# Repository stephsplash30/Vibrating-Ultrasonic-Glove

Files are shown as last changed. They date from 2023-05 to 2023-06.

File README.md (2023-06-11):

# Vibrating Ultrasonic Glove
Eric Zhu, Kate Saxen, and Katya Osipova

## Table of Contents
1. [Introduction](#Introduction)
2. [Initial Circuit](#Initial-Circuit)
3. [Final Design](#Final-Design)
4. [Testing Apparatus](#Testing-Apparatus)
5. [Sensor Mounting](#Sensor-Mounting)
6. [Adding Sensors](#Adding-Sensors)
7. [Initial Tests](#Initial-Tests)
8. [Mount Tests](#Mount-Tests)
9. [Hoodie Tests](#Hoodie-Tests)
10. [Conclusion](#Conclusion)

## Introduction 
For our project, we aim to create a vibrotactile tool that will provide feedback based on the distance to the nearest obstacle, serving as an ancillary device for people with low or no vision in addition to a white cane. The device could be used at home or in busier areas, such as a grocery store. We hope to expand usage to bustling streets. In such environments, white canes could take up too much space or may simply be unnecessary due to familiarity of the environment. Overall, the size of a white cane is the main disadvantage, as it can be a safety hazard to the user or the surrounding people. Additionally, the stigmatization of mobility aids such as the white cane makes those with disabilities less inclined to adopt it. By using this device as a replacement, or a supplement, precise distance information is gained, which is critical in mobility. Our goal is to be able to work as well as a white cane, while making our device more compact and seamless to use in comparison.



We will demonstrate the use of this device with ultrasonic sensing technology, which uses sound waves to measure distance; these waves are emitted at a frequency range too high for humans to hear. Ultrasonic waves do not interfere with radio and electromagnetic waves, used in other day-to-day devices, allowing for comfortable use in daily life.

Our device lies in a wide field of sensing technologies that have a plethora of applications in motion detection, distance measurement, and level gauge. For example, sonar technology is used in water with its high-frequency sound waves allowing for sound propagation. There are also depth-sensing technologies, like laser scanning or stereo cameras, which create a 3-D image of the surrounding environment. Laser scanning projects an infrared laser point/line onto an object and captures its reflection via a sensor. Stereo cameras operate with the use of multiple lenses that contain image sensors, creating a vision disparity. Both these devices utilize trigonometric triangulation and reflection angles to calculate distance and map a 3-D surface. Our project may have applications outside of its niche, contributing to the whole field of ultrasonic sensing technology.

## Initial Circuit
For our project's circuitry, we have two main circuits: one for the ultrasonic sensor and one for the vibrational motor. 

Ultrasonic sensors use ultrasonic sound waves which are waves of high amplitude, above the approximate upper limit of audible human range at 20 kHz. An ultrasonic sensor works by emitting sound waves from a transmitter module. When an emitted sound wave hits an object within the sensor's range, it is reflected back to the receiver module (Fig. 1). For our initial circuit setup, we connected an ultrasonic sensor (HC-SR04) to a breadboard. Using four wires, we connected the sensor to the Arduino. In order to run the code and power the Arduino, we connected it to a USB Type A to B port connected to a PC. The ultrasonic sensor has four pins: VCC, TRIG, ECHO, and GND. In addition, there is a transmitter module as well as a receiver module on either side of the sensor and a crystal oscillator as illustrated in (Fig. 2):



***Fig. 1:** The figure shows how sound waves travel between the transmitter and receiver modules of the ultrasonic sensor and how the waves are reflected off of an object back*



***Fig. 2:** The figure shows the ultrasonic sensor set up. It has four pins: VCC, Trig, Echo, and GND, which are located on the bottom of the diagram. On either side there is a transmitter module and a receiver module, and on the top of the diagram there is a transducer/crystal oscillator.*

Our circuit works by utilizing Pulse Width Modulation, PWM, to send out and receive pulse signals. The VCC pin (or Voltage Common Connector) supplies a 5 DC voltage from the 5 volt Arduino pin. The Trig pin (initially connected to Pin D11 on the Arduino) receives this pulse of voltage thus initiating the sensor to transmit 8 cycles of ultrasonic burst at 40 kHz for at least 10 microseconds. If there is an object within the sensor's range of 2 cm to 400 cm and measuring angle of 30 degrees, the waves will bounce back to the sensor. It is then  the receiver that detects the returned burst. The Echo pin (connected to Pin D10 on the Arduino) gets set to 5 volts and a delay for the period (width) is measured. When the width is measured, the distance can be calculated as they are proportional. Pins D10 and D11 are both digital I/O channels where PWM output is possible. We will later expand to use more pins as we add additional sensors. The GND pin works to ground the overall system. This process can be visualized in (Fig. 3), as it converts one large pulse into an acoustic burst, which is returned to the sensor. The gap between the Trigger and Echo allows us to convert that into a distance eventually. Distance can be found using the equation:

$$d=(v_s t)/2$$

$d$ is the distance to the object, $v_s$ is the speed of sound at approximately 343 m/s, and $t$ is the time between transmission and reception of the sound wave. In this way, the sensor, along with code, can calculate distance, which will be converted to electrical signal, causing the motor to vibrate. We are able to test using just one sensor and printing out the distance of the closest object repeatedly using the code written in `initial-1sensor-distance.ino`. This completes the initial ultrasonic sensor half of our circuit.



***Fig. 3:** The figure shows the use of the trigger and echo in an ultrasonic sensor. A pulse is sent out from the PWM pin, which is converted from a trigger into an acoustic burst that is sent out and returned and can vary depending on the distance of the nearest object. The gap between the outgoing and returning acoustic bursts is the PWM output from the echo pin, which can be converted into a distance. It is important to note that there is a needed delay between the pulses that are sent out for the sensor to work appropriately.*

The second circuit is the vibrational motor circuit. This circuit has more components. One end of the vibration motor (polarity can be disregarded) will get a direct power supply from the 3.3V pin of the Arduino, this will allow it to vibrate strongly. In parallel with the motor will be a diode that is reverse-biased. This serves to act as a surge protector for the Arduino as the motor produces voltage spikes as it rotates. Without the diode, the voltage surges could damage the Arduino. The capacitor, also in parallel with the motor, absorbs these voltage spikes. A transistor is placed in series with the motor, which provides it with current amplification as the Arduino provides a relatively weak power supply. Then, the motor is able to run more powerfully, allowing for more range of vibration depending on how close to an object the sensor is. Specifically, we used a N-channel MOSFET transistor that works with PWM in its saturated mode, which is when PWM enters its widest width (100% duty cycle), to drive the motor. A 1K ohm resistor is placed in series with the transistor so not too much current is being supplied to the motor. This end of the circuit is connected to the D3 pin of the Arduino, which is a channel that allows PWM. This digital pin will be set to output. Now, we have our motor circuitry completed In (Fig. 4), we can see the completed circuit with all three ultrasonic sensors:



***Fig. 4:** The figure shows the completed circuitry with both the ultrasonic sensors and vibrational motor circuit represented*

We are using PWM coupled with a low pass filter to create an analog output instead of digital to analog converter because Arduino doesn’t have a DAC. The low pass filter can be seen in (Fig. 5) where a resistor is placed in series with the capacitor. The low pass filter works to sequester harmonic frequencies that arise as the sound waves are traveling. The only signal we want to input into our motor is that of the carrier frequency, which is 40 kHz. The harmonic frequencies create a dominant force of uncertainty, which the low pass filter mitigates.



***Fig. 5:** The figure shows the vibrational motor circuit and emphasizes the low pass filter used. Overall, the motor circuit consists of a resistor, transistor, diode, and capacitor connected in the following way above.*

To work in tandem with the motor circuit we can connect either a buzzer or a LED to the D6 pin to allow for an alternative method of testing our circuit, which is much easier to tell a difference than vibration for data collection. We started initially with a buzzer, which eventually we switched to a LED due to the squeaky noise the buzzer produced.

## Final Design

With all of our physical components completed, we can begin to consider how we are going to put it all together. We came up with two possibilities; we could either mount or sensor to a belt or to our chest. We ruled out using the belt as it would likely place the sensor too low to sense anything at around eye-level, while it also may be blocked by an oversized tee or longer jacket. Thus, this leaves us with mounting on our chest. An easy way to mount our sensor onto the user is by using velcro. To do this, we mounted it directly onto a hoodie, using the hoodie as the housing system for our device. We are able to velcro our sensors onto our hoodie and then able to directly attach our motor onto each of the sleeves of our hoodie. The rest of the arduino circuitry was soldered together and kept in the hoodie pouch. The vibrational motor wire is fed through the hoodie’s body and arm to its sleeve where the motor itself  will vibrate.This enables us to compact our entire device to be within the hoodie, while also keeping it relatively lightweight of a system, placing it in areas that are able to carry the weight easier. Alternatively, we could have mounted the motor to a glove or a bracelet, but both of those solutions would have added weight to our system. The final design can be seen in the figure below:



***Fig. 6:** The figure shows the final design of our circuits as we implement it into our hoodie.*

## Testing Apparatus
In order to precisely measure our device’s detection range we created a stable apparatus where our mount was placed onto a wall with velcro. We set up two vertical mounting rods that each had a horizontal rod attached, which allowed us to secure our test object at a specific y axis for the vertical limit. The depth of the measurement is varied along the third axis, the z axis. During each test, the rod is slowly moved from the outside of the sensor’s range and brought to a position that is detectable by the sensor at a given z value. Similarly, we were able to test for left and right boundaries by turning the test object vertically and slowly moving it along the x axis in front of the sensor. All of our measurements were made relative to the mount’s center surface along multiple distances.

Mount test diagram

***Fig. 7:** The figure shows the mounting apparatus used to take all data for our project. It is important to note that we define (0,0) to be the center of the middle sensor for the mount. We move a thick meter stick ruler for the most effective test results.*

## Sensor Mounting
In order for the ultrasonic sensor circuit to work well, it must have a stable 3D printed PLA mount. Because our project is geared towards serving those with visibility impairments, it is of paramount importance that our design cover as much surface area in front of the user as possible. Therefore, the main design feature of our mount is the three angled faces each of about 15 degrees, meant to be occupied by three HC-SR04 sensors held strongly in place with four screws, which reduces the apparatus's vertical blindspots to a minimum. Another main feature of the mount is the hollow interior and an open strips on the top and middle face; we do not need one of the bottom face as it has direct access to the hoodie's pcoket. This provides us with the ability to feed the sensors wires through the mount and out the bottom. When attaching the mount to the hoodie, this makes it more convenient to connect the sensors to the microcontroller and thus, the vibration circuit, which will both be kept in the hoodie's pocket. The mount itself was made using a 3-D printer and a design program called Fusion 360. The mount design can be viewed in (Fig. 8):



***Fig. 8** The figure shows the mount that the ultrasonic sensors were placed on. The mounts faces are at angles of 15 degrees with respect to each other.*

Because of this new design, we had to edit our distance caluclation to include the tilt angle of the sensor. $$d=\frac{v_s t}{2\cos{\theta}}$$

This approach focuses on the horizontal distance that the nearest object is from our sensor, which equates to how close it is from hitting any part of our body. In essence, something 1 m away that's on the ground may actually be 0.5 m from tripping the user, rather than a wall 1 m away in front.

Our early designs included a flat faced mount with space for three sensors, but this design was omitted because there was too much overlap in the transmitter's wave emission and not enough dimension in measuring distance to an object. The design that we agreed upon increased the ability of the sensors to detect objects on the ground and near the user, as well as at waist, torso, and head heights.

As an aside, we know that the sensors lack measuring capabilities in front of the transducer. Because we want the vibrational motor to stop before the user hits an object, we are not concerned about this blindspot. Rather, it helps us in cutting off the vibrational motor, alerting the user that they are directly in front of an obstacle.

Initially, we had planned on attaching the sensors by sticking velcro to the back sides of them and the faces of the mount. This did not provide much stability as the velcro was not very strong and the sensors were not pointing outwards perpendicular to the face of the mount. Instead, we drilled the sensors into the mount with tiny screws. This provided a sturdy base as the sensors could not be shaken off the mount, and the emitted waves would be sent straight outward rather than at an offset angle.

## Adding Sensors

In attaching the sensors to the mount, they had to be prepped. We began by sodering off the ECHO, TRIG, GND, and VCC pins as they would not allow the sensors to lay flat on the mount's face as well as taking up unnecesary space in a small volume. In place of the pins, four long wires were sodered through the holes that the pins previously occupied.  



***Fig. 9:** The figure shows the pins with long wires sodered through them.*

Each VCC, TRIG, and GND wire from the three sensors are then threaded through the mount and respectively soldered together and placed in the same parts of the arduino as before with 1 sensor.



***Fig. 10:** The figure shows the various wires connecting all VCC, TRIG, and GND wires. All ECHO wires are free from one another.*

Each of the ECHO wires are then connected to independent digital I/O ports, the bottom is plugged into 5, the middle into 9, and the top into 10. By plugging in the three triggers into the same port to be triggered together, that allows the sensors to each send out a wave simultaneously, even though we only loop through one echo at a time. This process can be seen through the code in `initial-3sensor-1buzzer1motor.ino`, which works with the 3 sensors in tandem. It is important to note the delays within the code. If the delay is removed, the sensors take data too fast and will begin outputting strange values that are not representative of what is in front.

The electrical signals that will be controlling the vibrational motor will be receiving its input from data from the ultrasonic sensor

## Initial Tests
With our full circuit setup, we conduct our first initial test with the code writen in `initial-1sensor-1buzzer1motor.ino`. For this, we first begin tweaking the function we use to vibrate the motor. We use a piecewise function where under some given distance, $d_{min}$, the motor output is constant. Thus, we allow $f(x)=V_{max}$ for $x\lt d_{min}$. Now for larger $x$ values, we use an exponential decay function of the form $f(x)=V_{max}e^{-(x-d_{min})/c}$. For the Arduino, the full power of the system would have $V_{max} = 255$. We start off with $d_{min}=30$ and the constant $c$ determines how fast the power function decays. 

Voltage Output and Reported Distance vs Physical Distance

***Fig. 11:** The plot is shown gives us a distance vs. distance plot for the sensor's reported value and the physical distance on the left axis. Wee can then convert that into a voltage based on our piecewise function, which is shown on the right axis. We set our minimum distance for the voltage maximum to be set within 30cm, with the farther distances following an exponential decay.*

We start with a test that is important for understanding how our sensors work, that is data for the physical distance against the sensor reported distance. To do this, we move our thick meter stick forwards and backwards across 5cm intervals, taking an average of the reported values from the Serial Monitor. This process yields a plot as shown in (Fig. 11) with the left axis. From it, we see that it follows the expected value at low distances, but begins to deviate somewhat significantly towards the ends. However, at far distances, this deviation is caused by the naturally higher variability in the distance calculation the farther the ultrasonic waves have to travel. At farther distances, the effects of a slight shift in the calculation are much more minimal compared to at closer distances.

We do the same test, but wire the LED/buzzer circuitry to an oscilloscope to see how the physical distances are converted to a PWM percentage. From our code, we have our expected function that converts the distances exponentially. We see that in (Fig. 11) on the right axis that our data aligns with the expected output well, so the motor and LED circuit are working as we expect it to at any given distance.

Next, based off of our testing apparatus, we create a setup to sweep a squared thick meter stick both up and down and side to side while looking for a jump in the distance reported to locate the outer boundaries of the sensor in both the directly up and down direction and side to side direction. We will do this process for a set of distances: 20cm, 40cm, 57cm, and 77cm. We added tape to our setup to ensure reproducibility of our data.  Since we are given the supposed working range of the sensors, we can compare our results to the datasheet. With each of the distances we use, we can create a plot to visualize the working range in both directions.

Vertical working range of a single sensor

***Fig. 12:** The plot is shown for the working range of a single sensor in the up and down direction. The red points show the raw data and a linear regression is applied to both sides to estimate the working range up and down.*

As we see in (Fig. 12), there is a clear outward fanning shape for the vertical working range. This makes sense due to the shape of the sensors likely blocking some nearby waves while being able to accept a larger range from farther away. This works well for our project as we are focused on detecting objects farther away in order to alert the user of an incoming obstacle rather than detecting it too late. However, this makes it harder to compare our results to the values in the datasheet. We can calculate our working range in two ways. The first, we can use a linearization from the plot to map the working range. This yields an approximate value of 18 degrees. We alternatively calculate it using the end points of our plot as we are more focused on the working range farther away from our sensor. This yields an approximate value of 25 degrees. The datasheet provides that the working range should be 30 degrees, or 15 degrees in each direction. Thus, our calculation at a farther distance matches closer to the expected datasheet value, as there is some fall off in performance of the sensor from close distances. Additionally, it is important to note that there is a slightly uneven effectual range on the two sides of the sensor; it is able to detect more above the sensor than below.

Horizontal working range of a single sensor

***Fig. 13:** The plot is shown for the working range of a single sensor in the left and right direction. The red points show the raw data and a linear regression is applied to both sides to estimate the working range left and right.*

We do a similar plot for the horizontal working range shown in (Fig. 13), as we see a similar outward fanning shape, likely for the same reason as stated earlier. Again, we calulate the working range with the two methods. This first method yields a value of 14 degrees and the second method yields a value of 13 degrees. The working angle in this direction appears to be much smaller than the expected datasheet value and compared to the other direction. Looking at how we took our data, this may be atttributed to the orientation of the rod. Since we lay the rod vertically in front of the sensor, some of the waves may hit the rod but get reflected in a way that that does not allow for it to return to the sensor. Thus, if the rod were slightly turned, the distance it could be tracked may increase. It is likely because of this that the datasheet reports the effectual angle to be less than 15 degrees in every direction. This assumes that if the object is placed in the ideal orientation, it can be detected at an angle of up to 15 degrees, otherwise it is likely less.

## Mount Tests

To start off, we want to test how our mount actually works at comparing each of the sensors individually with the working range of the entire sensor. To do this, we can run our `initial-1sensor-distance.ino` code for each of the sensors, running the same initial test we did on 1 sensor, to map each of the sensors working ranges. We can make a plot of all of the independent ranges together, shown in (Fig. 14) and (Fig. 15).

Vertical working range of each sensor overlapped

***Fig. 14:** The figure shows the three sensors measured individually in the up and down direction relative to the middle of the respective sensor. The upper points are the maximum height and the bottom points are the minimum heights.*

Horizontal working range of each sensor

***Fig. 15:** The figure shows the three sensors measured individually in the left and right direction. The upper points are the maximum leftwards from the sensor and the bottom points are the maximum rightwards from the sensor.*

We notice that in the vertical direction in (Fig. 14), the sensors that tilt downwards have a slightly smaller working range, which may be due to the fact of the bouncing angle of the waves on a flat rod. Meanwhile, in the horizontal direction in (Fig. 15), there is the similar struggle of side to side wave deflection that the three working ranges mostly overlap. To better visualize the compounding of the three sensors, we can plot them relative to each other rather than relative to the appropriate sensor. When we test all three of our sensors together, we mark the middle to be the middle sensor, so we can set that to be the relative 0 for our plots in the vertical direction.

Vertical working range of each sensor overlapped

***Fig. 16:** The figure shows the three sensors measured individually in the up and down direction, each relative to the (0,0) set at the middle sensor. The upper points are the maximum height and the bottom points are the minimum heights.*

From (Fig. 16), we note that there is significant overlap between the sensors at a distance outside of 20cm. Because of this, we likely do not need to worry too much about physical blind spots, focusing more on the problem of waves being reflected away. The bottom sensor appears to add a minimal working range, likely due to the angles making it harder for it to allow for waves to reflect back for it to detect.

After testing each sensor individually, which was representative of a control group, we took measurements of all three sensors working together. We start off by doing the same test we did for the single sensor with the three sensor system, moving the rod side to side and up and down. Since this is our final mount, we measure at more data points to get a better picture of the shape of the working range. We once again can shade in the estimated working range of each, using a linear regression fit, to see that the working range of our three sensor system is greater in both the horizontal and vertical directions and left and right directions. This is seen in (Fig. 17) and (Fig. 18):

whole device vs single sensor vertical sensing ranges

***Fig. 17:** The figure shows the three sensors measured together in the up and down direction relative to the middle of the respective sensor. We then compare this to the single sensor data. We can once again sweep out an estimated working range for each of the sets of data.*

whole device vs single sensor horizontal sensing ranges

***Fig. 18:** The figure shows the three sensors measured together in the left and right direction relative to the middle of the respective sensor. We then compare this to the single sensor data. We can once again sweep out an estimated working range for each of the sets of data.*

From our previous tests, we notice that the orientation of the rod is very important. If the rod is angled in the right direction, it'll more likely reflect waves to hit the sensor. Thus, we can do the same side to side, up and down test, while being able to rotate the rod at a given location. This gives us the maximum working range with tilt, meaning any object within the working range with tilt has a possibility to be measured by the sensor. We can see from (Fig. 19) and (Fig. 20), the working ranges are much larger in both the horizontal and vertical directions. The tilt test helps clearly represent the increased working range for the vertical direction, greatly expanding our working range downwards, representing the mount that we use that has sensors angled downwards.

Vertical working range tilted vs not tilted

***Fig. 19:** The figure shows the three sensors measured together in the up and down direction while tilting and without tilting the rod. We can once again sweep out an estimated working range for each of the sets of data.*

Horizontal working range tilted vs not tilted

***Fig. 20:** The figure shows the three sensors measured together in the left and right direction while tilting and without tilting the rod. We can once again sweep out an estimated working range for each of the sets of data.*

## Hoodie Tests

Once we have our final design set up, we have to make some final tests with our hoodie in order to confirm that it works as expected for a user. For this, we implemented `final-3sensor-1motor.ino` as the onboard code that is run independent of plugging into a computer. Thus, at this stage we could test the hoodie on complete battery power. Here, we take a more qualitative approach and see if there are any bugs or issues with our setup. For this, the main issues we would need to test here, is tuning the parameters of our vibration power to best help the user stop before reaching an obstacle. Additionally, we need to test the effectiveness of the sensor being unobstructed by the human body and the feeling of the motor attached to the hoodie. 

In qualitative tests of our final design, we found that it did not always detect objects below waist level, such as bushes. When the waves hit a leaf that was tilted in a particular way, it was sometimes detectable. In addition, in order to precisely understand the boundaries the user is walking in, they must walk slower than a normal pace. Overall, our device works in the range that we want, but one has to move slowly in order to make the most use of the vibrational motor’s gradient. We notice that with practice, the user is able to quickly begin acclimating to our system, feeling differences in vibrations better, which may be difficult to differentiate initially.

## Conclusion

Overall, our hoodie works well to solve the problem we set out to conquer. However, in the future, we can test using different ultrasonic sensors, since we are limited by the ability of the sensors working range and the impact of the orientation of the object. From this, we would want to test out using an ultrasonic sensor with one transmitter and receiver channel combined. We would also want to use alternative ways of sensing such as infared or depth sensing cameras. We would also want to continue to integrate into our hoodie, to make the wiring and system more compact. For the vibration output circuit, we want to test integration into a bracelet or glove to provide the user with more feedback, or alternatively, using audio output in ears. Our project lays down the framework to one day replace the use of white canes, making it a more accessible mobility aid to those with low to no vision.

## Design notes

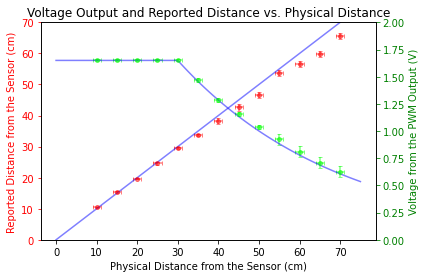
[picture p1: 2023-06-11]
graphs/Voltage Output and Reported Distance vs. Physical Distance.png

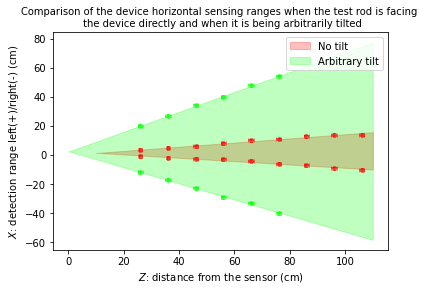
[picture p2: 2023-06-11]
graphs/Horizontal working range tilted vs not tilted.png

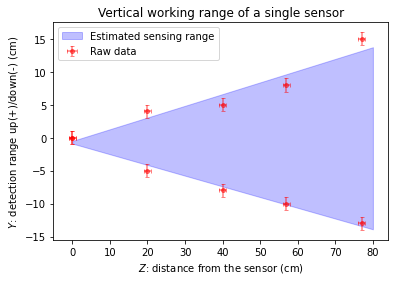
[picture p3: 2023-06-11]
graphs/Vertical working range of a single sensor.png

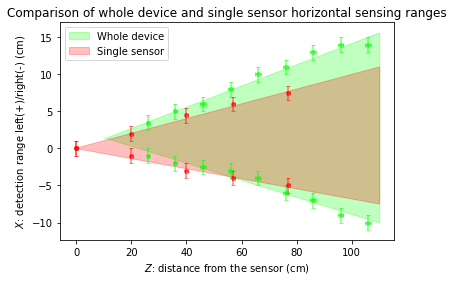
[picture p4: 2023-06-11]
graphs/whole device vs single sensor horizontal sensing ranges.png

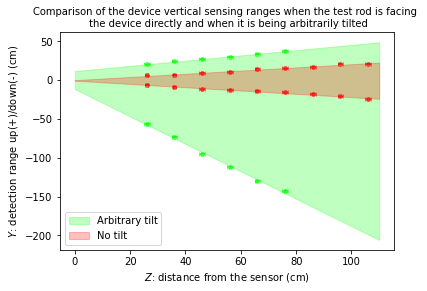
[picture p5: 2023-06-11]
graphs/Vertical working range tilted vs not tilted.png

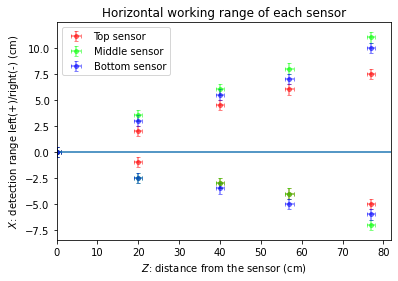
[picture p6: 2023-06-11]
graphs/Horizontal working range of each sensor.png

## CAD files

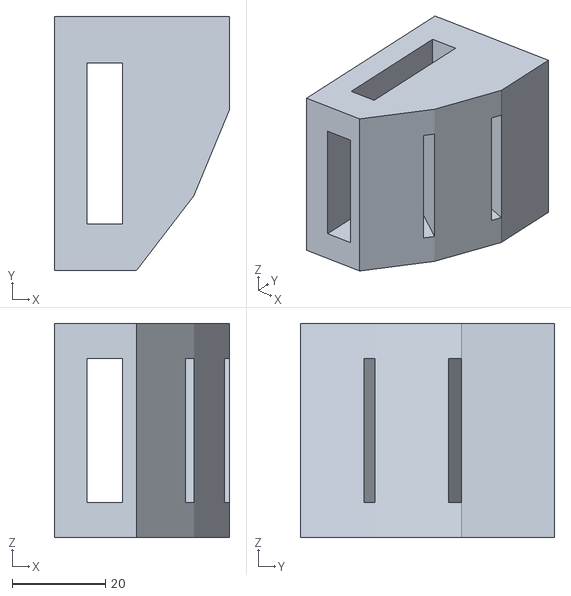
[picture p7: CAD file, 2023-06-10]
mount design/Sensor mount.stl
37.7 x 54.6 x 46.0

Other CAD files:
mount design/Sensor mount.obj

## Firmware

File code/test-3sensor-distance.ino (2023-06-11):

#define Trig 11 //Use one trigger and 3 echos to be able to simultaenously trigger
#define Echo1 10
#define Echo2 9
#define Echo3 5
#define Buzzer 6
#define Motor 3 

void setup()
{ 
  pinMode(Trig, OUTPUT);
  pinMode(Echo1, INPUT);
  pinMode(Echo2, INPUT);
  pinMode(Echo3, INPUT);
  pinMode(Buzzer, OUTPUT);
  pinMode(Motor, OUTPUT);
}

void loop()
{ 
  float dist1, dist2, dist3, dist; 
  float timetaken[3];
  int echo[3]={Echo1,Echo2,Echo3};
  for(int i = 0; i<3; i++){
    digitalWrite(Trig, LOW); 
    delayMicroseconds(20); 
    digitalWrite(Trig, HIGH);
    delayMicroseconds(10); 
    digitalWrite(Trig, LOW);
    timetaken[i] = (float) pulseIn(echo[i], HIGH);
    
    delay(50); 
  }
  dist1 = ((timetaken[0]/2)*340)/10000;//By the formula- distance=(time/2)*speed of sound
  dist2 = cos(15*M_PI/180)*((timetaken[1]/2)*340)/10000;//By the formula- distance=(time/2)*speed of sound
  dist3 = cos(30*M_PI/180)*((timetaken[2]/2)*340)/10000;//By the formula- distance=(time/2)*speed of sound
  dist = minimum(dist1, dist2, dist3);

  Serial.begin(9600);
  Serial.print("Distance: ");
  Serial.print(dist);
  //Serial.println(asctime());
  Serial.print("cm");
  Serial.print("Distance1: ");
  Serial.print(dist1);
  Serial.print("cm");
  Serial.print("Distance2: ");
  Serial.print(dist2);
  Serial.print("cm");
  Serial.print("Distance3: ");
  Serial.print(dist3);
  Serial.println("cm");
  //delay(100);
}

float minimum(float a, float b, float c){ float min;
  min=a;
  if(b<min&&b>0){
    min=b;
  }
  if(c<min&&c>0){
    min=c;
  }
  return min;
}
//add a transistor parallel to the motor, use the diagram on the document Kate made. 
//edit distance variable to get linear distance to the person
//in future edit the code so different motors vibrate at different strength, each motor corresponds with a sensor.

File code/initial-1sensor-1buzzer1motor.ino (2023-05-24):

#define Trig 11 //Use one trigger and 3 echos to be able to simultaenously trigger
#define Echo1 5
#define Buzzer 3
#define Motor 6

void setup()
{ 
  pinMode(Trig, OUTPUT);
  pinMode(Echo1, INPUT);
  pinMode(Buzzer, OUTPUT);
  pinMode(Motor, OUTPUT);
}

void loop()
{ 
  float dist1, timetaken1; 
  digitalWrite(Trig, LOW); 
  delayMicroseconds(20); 
  digitalWrite(Trig, HIGH);
  delayMicroseconds(10); 
  digitalWrite(Trig, LOW);
  timetaken1 = (float) pulseIn(Echo1, HIGH);
  dist1 = ((timetaken1/2)*340)/10000;//By the formula- distance=(time/2)*speed of sound
  Serial.begin(9600);
  Serial.print("Distance: ");
  Serial.print(dist1);
  Serial.println("cm");

  if (dist1< 150) //If distance is less than 100, motor is activated
  {
    if (dist1 < 30){
      analogWrite(Buzzer, 255/5);
      analogWrite(Motor, 255/2);
    }
    else{
    //analogWrite(Buzzer, 255*(1 - (dist1-10)/90)/10); // turn on motor on full power (range is 0 - 255)
      analogWrite(Motor, (255/2)*pow(M_E, (-1)*(dist1-30)/40));
      analogWrite(Buzzer, (255/5)*pow(M_E, (-1)*(dist1-30)/20));
    }
  }
  else{
    analogWrite(Motor, 0);
    analogWrite(Buzzer, 0);
  }
  delay(50);
}
//add a transistor parallel to the motor, use the diagram on the document Kate made. 
//edit distance variable to get linear distance to the person
//in future edit the code so different motors vibrate at different strength, each motor corresponds with a sensor.

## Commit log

2023-05-03 Initial code for distance measurment for ultrasonic sensor.
2023-05-03 Create Initial Circuits
2023-05-03 Update Initial Circuits
2023-05-08 added code to include buzzer and motor
2023-05-10 working with 3 sensors
2023-05-17 tweaked files and added new 3 sensor distance file
2023-05-23 Code for 1 sensor working range
2023-05-31 added mount tests
2023-06-09 Create device_detection_range
2023-06-09 Create device_detection_range_wide
2023-06-10 Update device_detection_range
2023-06-10 Update device_detection_range_wide
2023-06-10 Added 3D model of the mount
    [Sensor mount.obj, Sensor mount.stl]
